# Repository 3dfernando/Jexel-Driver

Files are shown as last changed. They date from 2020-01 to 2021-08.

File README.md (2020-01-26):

# Jexel-Driver
A PIC32-based programmable function generator and solenoid driver with 108 channels. Check 04 - Documentation/SigGen_Board_Datasheet_R02.pdf for usage instructions.

This implementation employs a PIC32MZ2048ECH144 microcontroller to generate 108 independently programmable square waves. The computer interface is an FTDI FT232 chip, which becomes a USB-Serial interface and appears in the computer as a regular COM port. Sending strings to the COM port with the right settings will program/activate the "jexels" (short for jet-pixels), allowing interesting combinations. 

The current effective sampling rate is 49.8kS/s (measured with a scope given the delays of the program), remembering each channel is one-bit. There's a delay of 200ns (one cycle) between the update of each port in the uC. Since there's 10 ports being used, a total 1.8us delay exists between PORTA and PORTK. I deemed this delay insignificant since the maximum square wave drive frequency intended was 200Hz, thus rendering this maximum 1.8us delay less than 0.13 degrees error in the phase between the waves.

Let me know if you find this useful. Things that could be done to improve the application (which I decided not to):
-Increase data density in the serial port to allow a live data stream from the PC instead of a one-off program
-Make drivers with different capacities (more amps, higher voltage, etc) for different solenoid needs
-Isolate better the 24V line from the PIC (i.e., have a connector directly to the driver board).

I used MPLAB X IPE for the microcontroller program. EasyEDA (yes, I'm ashamed) for the electronic boards and JLCPCB for the printing service. The boards were designed to be hand-assembled (I used the hot plate method with solder paste - see here an example https://www.youtube.com/watch?v=2gkZX0r4cvQ).

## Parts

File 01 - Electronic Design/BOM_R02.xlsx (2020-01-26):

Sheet: Motherboard
108-Channel Signal Generator - BOM
Schematic No. | Part Name | Digikey PN | Unit Price | Digikey Link
C1 | CAP CER 0.1UF 16V Y5V 0603 | ‎CL10F104ZO8NNNC‎ | $0.04 | https://www.digikey.com/product-detail/en/samsung-electro-mechanics/CL10F104ZO8NNNC/1276-1258-1-ND/3889344
C2 | CAP CER 0.1UF 16V Y5V 0603 | ‎CL10F104ZO8NNNC‎ | $0.04 | https://www.digikey.com/product-detail/en/samsung-electro-mechanics/CL10F104ZO8NNNC/1276-1258-1-ND/3889344
C3 | CAP CER 0.1UF 16V Y5V 0603 | ‎CL10F104ZO8NNNC‎ | $0.04 | https://www.digikey.com/product-detail/en/samsung-electro-mechanics/CL10F104ZO8NNNC/1276-1258-1-ND/3889344
C4 | CAP CER 0.1UF 16V Y5V 0603 | ‎CL10F104ZO8NNNC‎ | $0.04 | https://www.digikey.com/product-detail/en/samsung-electro-mechanics/CL10F104ZO8NNNC/1276-1258-1-ND/3889344
C5 | CAP CER 0.1UF 16V Y5V 0603 | ‎CL10F104ZO8NNNC‎ | $0.04 | https://www.digikey.com/product-detail/en/samsung-electro-mechanics/CL10F104ZO8NNNC/1276-1258-1-ND/3889344
C6 | CAP CER 0.1UF 16V Y5V 0603 | ‎CL10F104ZO8NNNC‎ | $0.04 | https://www.digikey.com/product-detail/en/samsung-electro-mechanics/CL10F104ZO8NNNC/1276-1258-1-ND/3889344
C7 | CAP CER 0.1UF 16V Y5V 0603 | ‎CL10F104ZO8NNNC‎ | $0.04 | https://www.digikey.com/product-detail/en/samsung-electro-mechanics/CL10F104ZO8NNNC/1276-1258-1-ND/3889344
C8 | CAP CER 0.1UF 16V Y5V 0603 | ‎CL10F104ZO8NNNC‎ | $0.04 | https://www.digikey.com/product-detail/en/samsung-electro-mechanics/CL10F104ZO8NNNC/1276-1258-1-ND/3889344
C9 | CAP CER 0.1UF 16V Y5V 0603 | ‎CL10F104ZO8NNNC‎ | $0.04 | https://www.digikey.com/product-detail/en/samsung-electro-mechanics/CL10F104ZO8NNNC/1276-1258-1-ND/3889344
C10 | CAP CER 0.1UF 16V Y5V 0603 | ‎CL10F104ZO8NNNC‎ | $0.04 | https://www.digikey.com/product-detail/en/samsung-electro-mechanics/CL10F104ZO8NNNC/1276-1258-1-ND/3889344
C11 | CAP CER 10000PF 50V X7R 0603 | ‎CL10B103KB8NNNC | $0.10 | https://www.digikey.com/product-detail/en/samsung-electro-mechanics/CL10B103KB8NNNC/1276-1009-1-ND/3889095
C12 | CAP CER 0.1UF 16V Y5V 0603 | ‎CL10F104ZO8NNNC‎ | $0.04 | https://www.digikey.com/product-detail/en/samsung-electro-mechanics/CL10F104ZO8NNNC/1276-1258-1-ND/3889344
C13 | CAP CER 0.1UF 16V Y5V 0603 | ‎CL10F104ZO8NNNC‎ | $0.04 | https://www.digikey.com/product-detail/en/samsung-electro-mechanics/CL10F104ZO8NNNC/1276-1258-1-ND/3889344
C14 | CAP CER 15PF 50V C0G/NP0 0603 | ‎0603N150J500CT | $0.10 | https://www.digikey.com/product-detail/en/walsin-technology-corporation/0603N150J500CT/1292-1487-1-ND/9355491
C15 | CAP CER 15PF 50V C0G/NP0 0603 | ‎0603N150J500CT | $0.10 | https://www.digikey.com/product-detail/en/walsin-technology-corporation/0603N150J500CT/1292-1487-1-ND/9355491
ICSP | CONN HEADER R/A 6POS 2.54MM | ‎61300611021 | $0.54 | https://www.digikey.com/product-detail/en/w-rth-elektronik/61300611021/732-5339-ND/4846832
J1 | CONN PWR JACK 2X5.5MM SOLDER | ‎PJ-037AH | $0.71 | https://www.digikey.com/product-detail/en/cui-devices/PJ-037AH/CP-037AH-ND/1644547
L1 | FERRITE BEAD 40 OHM 0805 1LN | ‎MI0805K400R-10‎ | $0.21 | https://www.digikey.com/product-detail/en/laird-signal-integrity-products/MI0805K400R-10/240-2389-1-ND/806749
LED1 | LED GREEN DIFFUSED 1206 SMD | ‎QTLP650D4TR | $0.53 | https://www.digikey.com/product-detail/en/everlight-electronics-co-ltd/QTLP650D4TR/1080-1419-1-ND/2676153
PORT1 | CONN RCPT 26POS 0.05 GOLD PCB | ‎20021311-00026T4LF | $2.13 | https://www.digikey.com/product-detail/en/amphenol-icc-fci/20021311-00026T4LF/609-3762-ND/2209113
PORT2 | CONN RCPT 26POS 0.05 GOLD PCB | ‎20021311-00026T4LF | $2.13 | https://www.digikey.com/product-detail/en/amphenol-icc-fci/20021311-00026T4LF/609-3762-ND/2209113
PORT3 | CONN RCPT 26POS 0.05 GOLD PCB | ‎20021311-00026T4LF | $2.13 | https://www.digikey.com/product-detail/en/amphenol-icc-fci/20021311-00026T4LF/609-3762-ND/2209113
PORT4 | CONN RCPT 26POS 0.05 GOLD PCB | ‎20021311-00026T4LF | $2.13 | https://www.digikey.com/product-detail/en/amphenol-icc-fci/20021311-00026T4LF/609-3762-ND/2209113
PORT5 | CONN RCPT 26POS 0.05 GOLD PCB | ‎20021311-00026T4LF | $2.13 | https://www.digikey.com/product-detail/en/amphenol-icc-fci/20021311-00026T4LF/609-3762-ND/2209113
PORT6 | CONN RCPT 26POS 0.05 GOLD PCB | ‎20021311-00026T4LF | $2.13 | https://www.digikey.com/product-detail/en/amphenol-icc-fci/20021311-00026T4LF/609-3762-ND/2209113
R1 | RES SMD 1K OHM 5% 1/4W 0603 | ‎ESR03EZPJ102‎ | $0.10 | https://www.digikey.com/product-detail/en/rohm-semiconductor/ESR03EZPJ102/RHM1.0KDCT-ND/1762924
R2 | RES 10K OHM 1% 1/8W 0603 | ‎RNCP0603FTD10K0 | $0.10 | https://www.digikey.com/product-detail/en/stackpole-electronics-inc/RNCP0603FTD10K0/RNCP0603FTD10K0CT-ND/2240478
R3 | RES SMD 270 OHM 0.5% 1/10W 0805 | ‎RR1220P-271-D | $0.11 | https://www.digikey.com/product-detail/en/susumu/RR1220P-271-D/RR12P270DCT-ND/432816
R4 | RES SMD 270 OHM 0.5% 1/10W 0805 | ‎RR1220P-271-D | $0.11 | https://www.digikey.com/product-detail/en/susumu/RR1220P-271-D/RR12P270DCT-ND/432816
R5 | RES SMD 270 OHM 0.5% 1/10W 0805 | ‎RR1220P-271-D | $0.11 | https://www.digikey.com/product-detail/en/susumu/RR1220P-271-D/RR12P270DCT-ND/432816
RX | LED GREEN DIFFUSED 1206 SMD | ‎QTLP650D4TR | $0.53 | https://www.digikey.com/product-detail/en/everlight-electronics-co-ltd/QTLP650D4TR/1080-1419-1-ND/2676153
TX | LED GREEN DIFFUSED 1206 SMD | ‎QTLP650D4TR | $0.53 | https://www.digikey.com/product-detail/en/everlight-electronics-co-ltd/QTLP650D4TR/1080-1419-1-ND/2676153
U1 | IC MCU 32BIT 2MB FLASH 144LQFP | ‎PIC32MZ2048ECH144-I/PL | $13.07 | https://www.digikey.com/product-detail/en/microchip-technology/PIC32MZ2048ECH144-I-PL/PIC32MZ2048ECH144-I-PL-ND/4500847
U11 | CONN RCPT USB2.0 MICRO B SMD R/A | ‎10118193-0001LF | $0.43 | https://www.digikey.com/product-detail/en/amphenol-icc-fci/10118193-0001LF/609-4616-1-ND/2785380
U8 | IC USB FS SERIAL UART 28-SSOP | ‎FT232RL-REEL‎ | $4.50 | https://www.digikey.com/product-detail/en/ftdi-future-technology-devices-international-ltd/FT232RL-REEL/768-1007-1-ND/1836402
USB_RX | PC TEST POINT NATURAL | ‎S2751-46R | $0.26 | https://www.digikey.com/product-detail/en/harwin-inc/S2751-46R/952-2664-1-ND/5250501
USB_TX | PC TEST POINT NATURAL | ‎S2751-46R | $0.26 | https://www.digikey.com/product-detail/en/harwin-inc/S2751-46R/952-2664-1-ND/5250501
Y1 | CRYSTAL 16.0000MHZ 18PF SMD | ‎ABLS-16.000MHZ-B4-T‎ | $0.36 | https://www.digikey.com/product-detail/en/abracon-llc/ABLS-16.000MHZ-B4-T/535-10226-1-ND/2184261
Total Cost |  |  | $35.98

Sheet: Driver Board
36-Channel Solenoid Driver - BOM
Schematic No. | Part Name | Digikey PN | Unit Price | Digikey Link
P1 | CONN HEADER VERT 26POS 1.27MM | ‎20021111-00026T4LF | $1.52 | https://www.digikey.com/product-detail/en/amphenol-icc-fci/20021111-00026T4LF/609-3720-ND/2209092
P2 | CONN HEADER VERT 26POS 1.27MM | ‎20021111-00026T4LF | $1.52 | https://www.digikey.com/product-detail/en/amphenol-icc-fci/20021111-00026T4LF/609-3720-ND/2209092
U1 | IC PWR DRIVER N-CHAN 1:1 16TSSOP | ‎TPL7407LPWR | $0.68 | https://www.digikey.com/product-detail/en/texas-instruments/TPL7407LPWR/296-37285-1-ND/4733034
U2 | IC PWR DRIVER N-CHAN 1:1 16TSSOP | ‎TPL7407LPWR | $0.68 | https://www.digikey.com/product-detail/en/texas-instruments/TPL7407LPWR/296-37285-1-ND/4733034
U3 | IC PWR DRIVER N-CHAN 1:1 16TSSOP | ‎TPL7407LPWR | $0.68 | https://www.digikey.com/product-detail/en/texas-instruments/TPL7407LPWR/296-37285-1-ND/4733034
U4 | IC PWR DRIVER N-CHAN 1:1 16TSSOP | ‎TPL7407LPWR | $0.68 | https://www.digikey.com/product-detail/en/texas-instruments/TPL7407LPWR/296-37285-1-ND/4733034
U5 | IC PWR DRIVER N-CHAN 1:1 16TSSOP | ‎TPL7407LPWR | $0.68 | https://www.digikey.com/product-detail/en/texas-instruments/TPL7407LPWR/296-37285-1-ND/4733034
U6 | IC PWR DRIVER N-CHAN 1:1 16TSSOP | ‎TPL7407LPWR | $0.68 | https://www.digikey.com/product-detail/en/texas-instruments/TPL7407LPWR/296-37285-1-ND/4733034
F1 | PTC RESET FUSE 30V 300MA 1812 | ‎0ZCG0030FF2C | $0.13 | https://www.digikey.com/product-detail/en/bel-fuse-inc/0ZCG0030FF2C/507-1758-1-ND/4156199
F2 | PTC RESET FUSE 30V 300MA 1812 | ‎0ZCG0030FF2C | $0.13 | https://www.digikey.com/product-detail/en/bel-fuse-inc/0ZCG0030FF2C/507-1758-1-ND/4156199
F3 | PTC RESET FUSE 30V 300MA 1812 | ‎0ZCG0030FF2C | $0.13 | https://www.digikey.com/product-detail/en/bel-fuse-inc/0ZCG0030FF2C/507-1758-1-ND/4156199
F4 | PTC RESET FUSE 30V 300MA 1812 | ‎0ZCG0030FF2C | $0.13 | https://www.digikey.com/product-detail/en/bel-fuse-inc/0ZCG0030FF2C/507-1758-1-ND/4156199
F5 | PTC RESET FUSE 30V 300MA 1812 | ‎0ZCG0030FF2C | $0.13 | https://www.digikey.com/product-detail/en/bel-fuse-inc/0ZCG0030FF2C/507-1758-1-ND/4156199
F6 | PTC RESET FUSE 30V 300MA 1812 | ‎0ZCG0030FF2C | $0.13 | https://www.digikey.com/product-detail/en/bel-fuse-inc/0ZCG0030FF2C/507-1758-1-ND/4156199
J1 | CONN HEADER SMD 12POS 1.5MM | ‎0874371243 | $1.63 | https://www.digikey.com/product-detail/en/molex/0874371243/WM7671CT-ND/717663
J2 | CONN HEADER SMD 12POS 1.5MM | ‎0874371243 | $1.63 | https://www.digikey.com/product-detail/en/molex/0874371243/WM7671CT-ND/717663
J3 | CONN HEADER SMD 12POS 1.5MM | ‎0874371243 | $1.63 | https://www.digikey.com/product-detail/en/molex/0874371243/WM7671CT-ND/717663
J4 | CONN HEADER SMD 12POS 1.5MM | ‎0874371243 | $1.63 | https://www.digikey.com/product-detail/en/molex/0874371243/WM7671CT-ND/717663
J5 | CONN HEADER SMD 12POS 1.5MM | ‎0874371243 | $1.63 | https://www.digikey.com/product-detail/en/molex/0874371243/WM7671CT-ND/717663
J6 | CONN HEADER SMD 12POS 1.5MM | ‎0874371243 | $1.63 | https://www.digikey.com/product-detail/en/molex/0874371243/WM7671CT-ND/717663
Total Cost |  |  | $17.67
Other parts for making cables to connect to solenoids (for 36 channels)
Qty | Part Name | Digikey PN | Unit Price | Digikey Link
6 | CONN HOUSING 12POS 1.5MM W/RAMP | ‎87439-1200 | $0.38 | https://www.digikey.com/product-detail/en/molex/0874391200/23-0874391200-ND/561775
72 | PICO-SPOX 300MM 24AWG PRE-CRIMPE | ‎0797581007 | $0.86 | https://www.digikey.com/product-detail/en/molex/0797581007/WM15690-ND/6564337
36 | CONN HOUSING 2POS 1.5MM W/RAMP | ‎0874390200 | $0.15 | https://www.digikey.com/product-detail/en/molex/0874390200/WM2086-ND/561765
Total Cost |  |  | $69.60

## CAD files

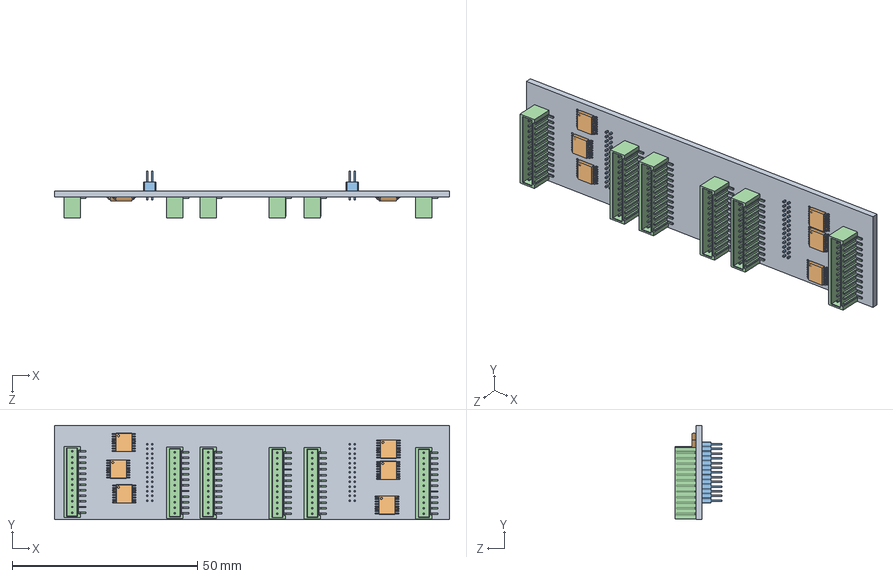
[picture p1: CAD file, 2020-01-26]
02 - 3D Model/01 - Solenoid Driver Board/Driver Board Assembly.SLDASM
106.7 x 25.4 x 12.8 mm
Driver PCB
User Library-TSSOP-16-1 x 6
2002111100026T4LF x 2
Pico-Spox 12w x 6

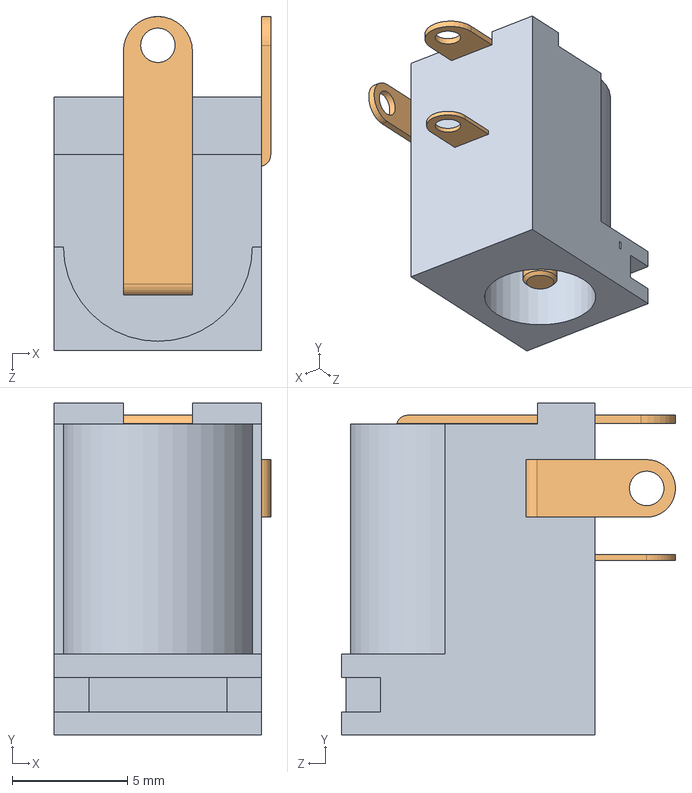
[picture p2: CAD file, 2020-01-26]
02 - 3D Model/02 - Motherboard/Components/User Library-PJ-002AH.sldasm
9.40 x 14.4 x 14.5 mm
User Library-PJ-002AH_Body
User Library-PJ-002AH_Pad

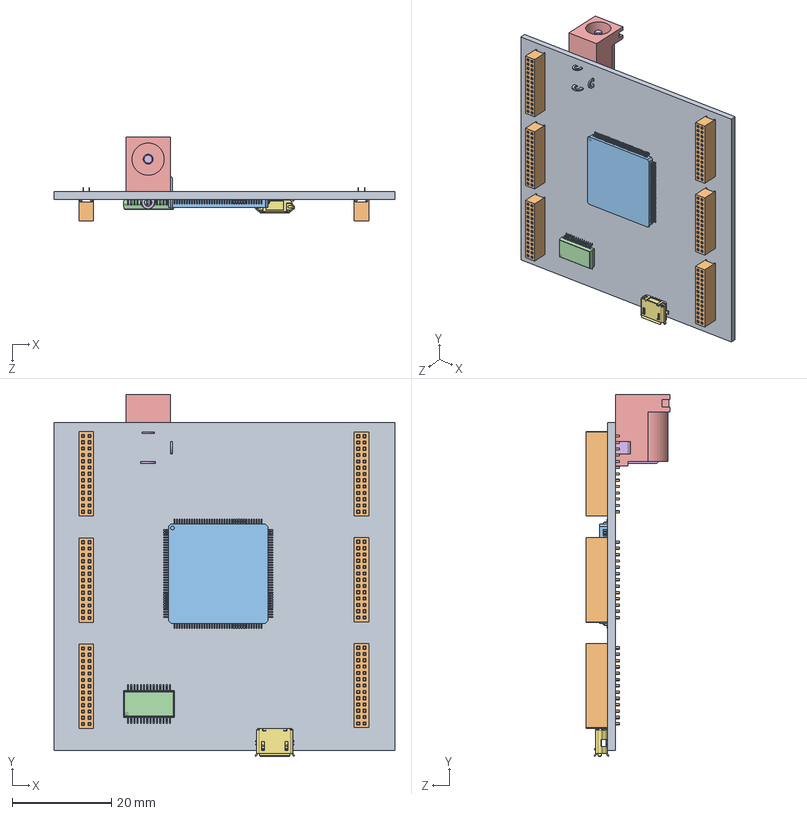
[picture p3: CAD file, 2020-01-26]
02 - 3D Model/02 - Motherboard/Motherboard Assembly.SLDASM
68.6 x 72.9 x 17.0 mm
Motherboard PCB
Header 26 Female x 6
User Library-TQFP144-1
User Library-SSOP-28-1
User Library-PJ-002AH_Body
User Library-PJ-002AH_Pad
usb_mc_2_b_smd

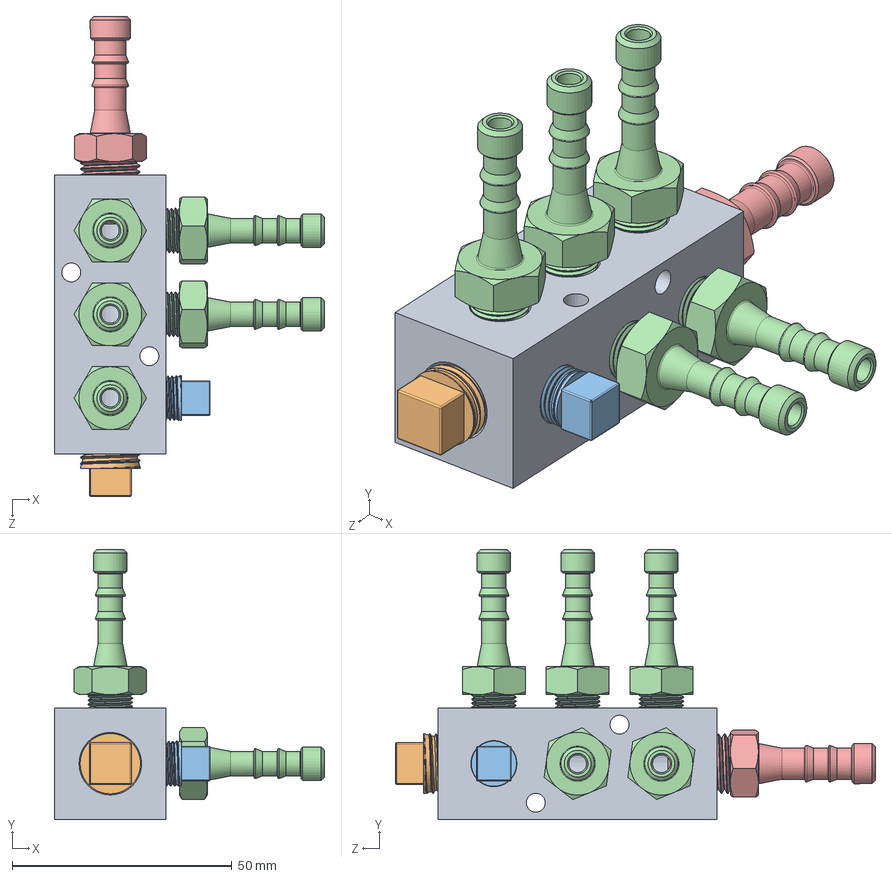
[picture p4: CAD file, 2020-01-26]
02 - 3D Model/03 - Pipelines/Ballast Assembly.SLDASM
61.4 x 61.4 x 109.2 mm
5469K210_BLACK ANODIZED ALUMINUM MANIFOLD
Aluminium Plug 1-4
Aluminium Plug 1-8
Hose Adaptor 1-8 x 1-4 x 5
Hose Adaptor 1-4 x 5-16

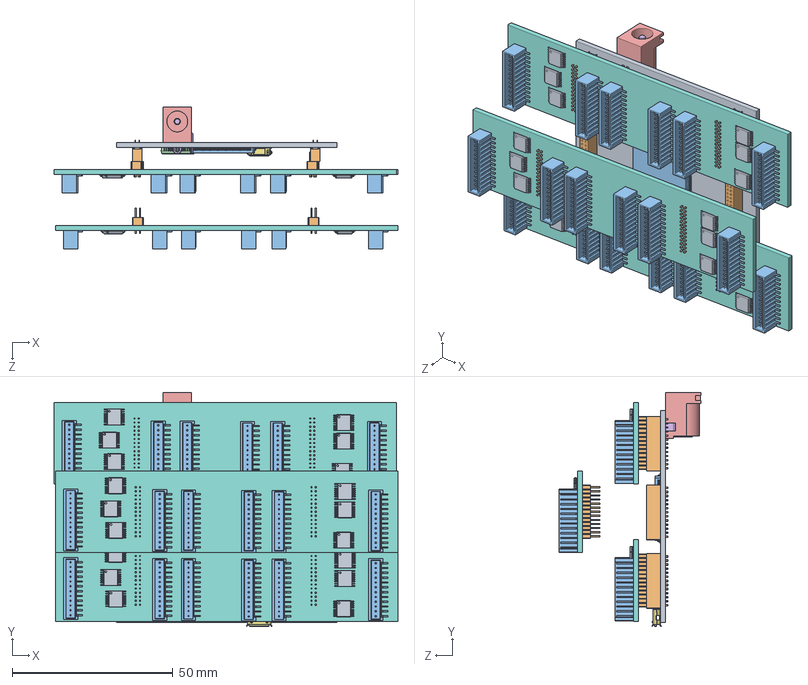
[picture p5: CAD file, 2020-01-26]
02 - 3D Model/Electronic Driver Assembly.SLDASM
107.1 x 72.9 x 44.2 mm
Motherboard PCB
Header 26 Female x 6
User Library-TQFP144-1
User Library-SSOP-28-1
User Library-PJ-002AH_Body
User Library-PJ-002AH_Pad
usb_mc_2_b_smd
Driver PCB x 3
User Library-TSSOP-16-1 x 18
2002111100026T4LF x 6
Pico-Spox 12w x 18

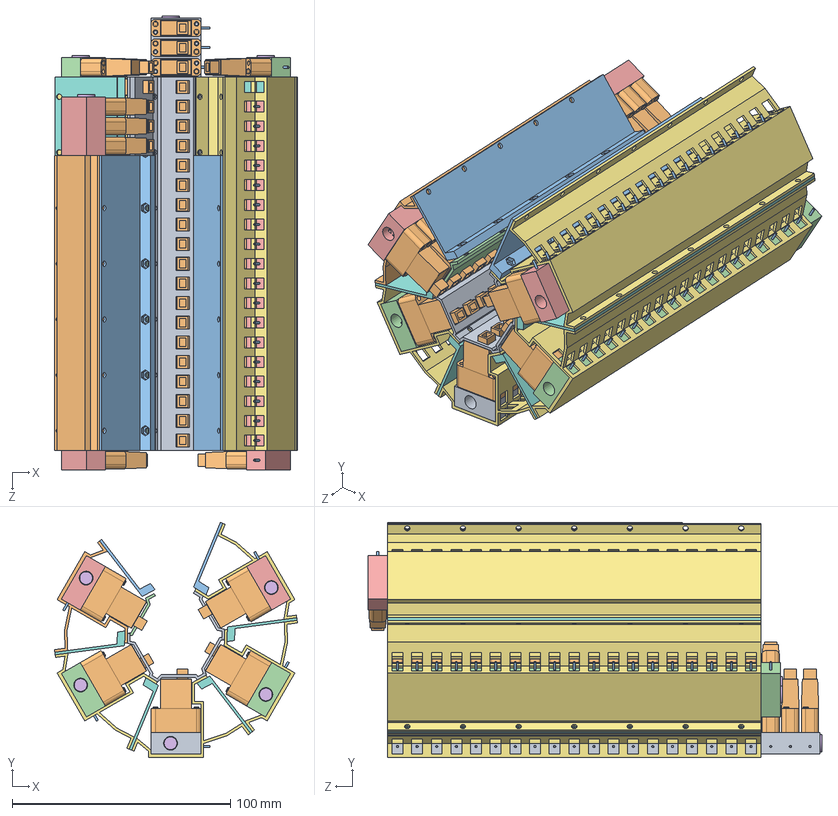
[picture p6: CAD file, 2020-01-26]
02 - 3D Model/Manifold Assembly Assembly.SLDASM
111.4 x 107.8 x 208.0 mm
Manifold 01 R00
Microvalv x 100
Tubing_1 x 100
Manifold 02 R00 x 2
Manifold 03 R00 x 2
EndPlug x 5
Valve Support Channel 2 x 4
Valve Support Channel 1 x 3
Valve Support Channel 3 x 3
Valve Support Channel Shorter 1 x 2
Valve Support Channel Shorter 2 x 2
Valve Support Channel Shorter 3 x 2

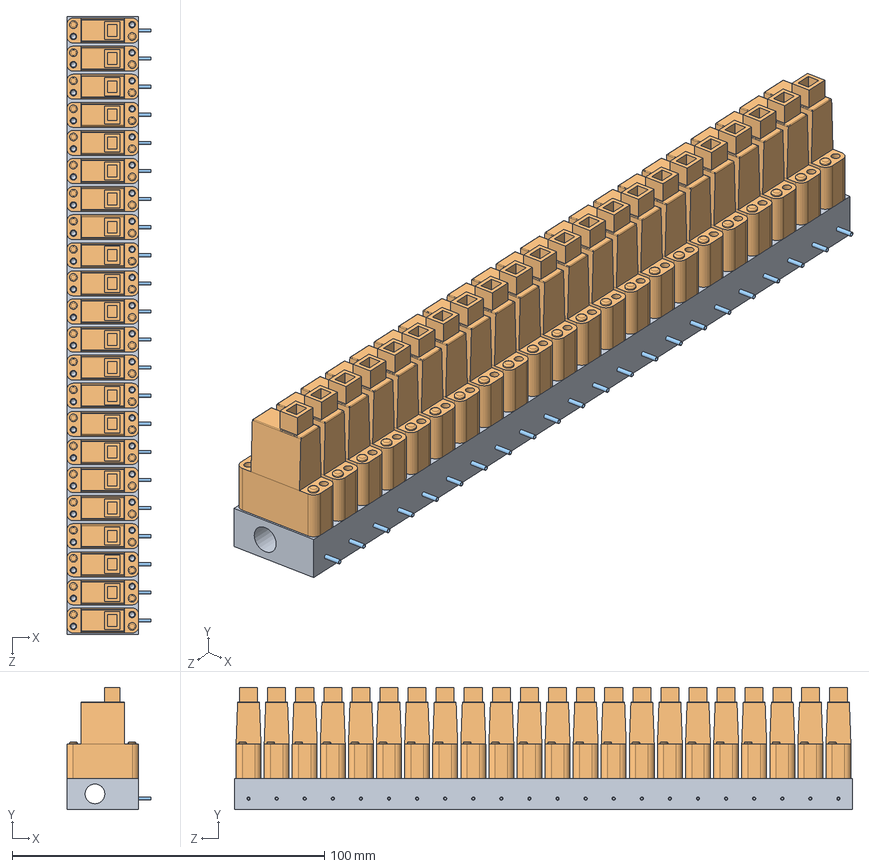
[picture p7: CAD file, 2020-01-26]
02 - 3D Model/Manifold Assembly 01.SLDASM
27.0 x 39.1 x 198.0 mm
Manifold 01 R00
Microvalv x 22
Tubing_1 x 22

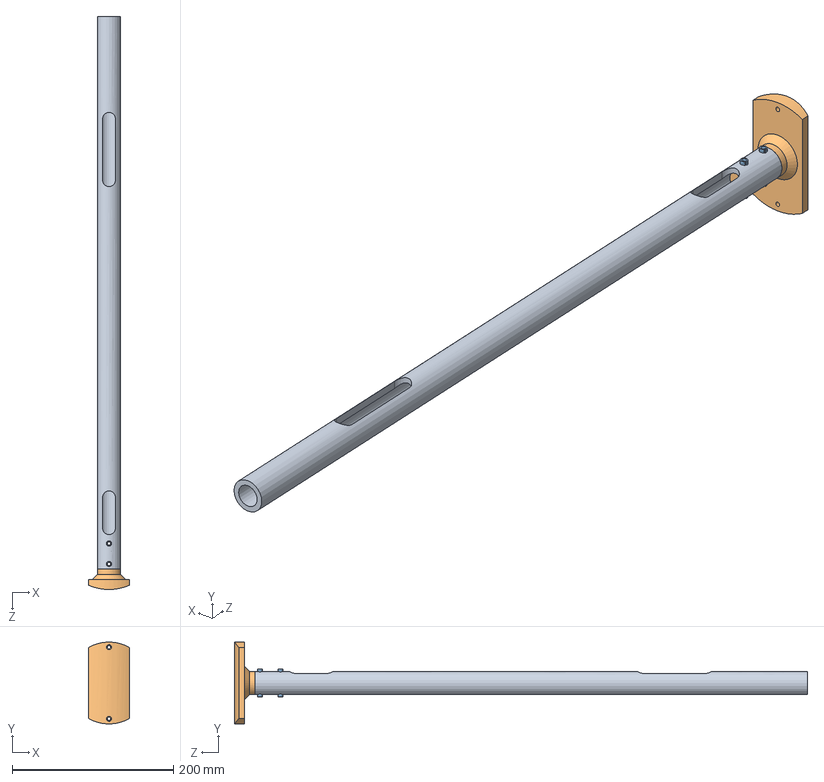
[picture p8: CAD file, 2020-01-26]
02 - 3D Model/lofted_cyl_strut.SLDASM
50.8 x 101.6 x 711.2 mm
Lofted_cyl_support_strut
Lofted_cyl_support_flange_v2
92383A750_TYPE 420 STAINLESS STEEL SLOTTED SPRING PIN x 2

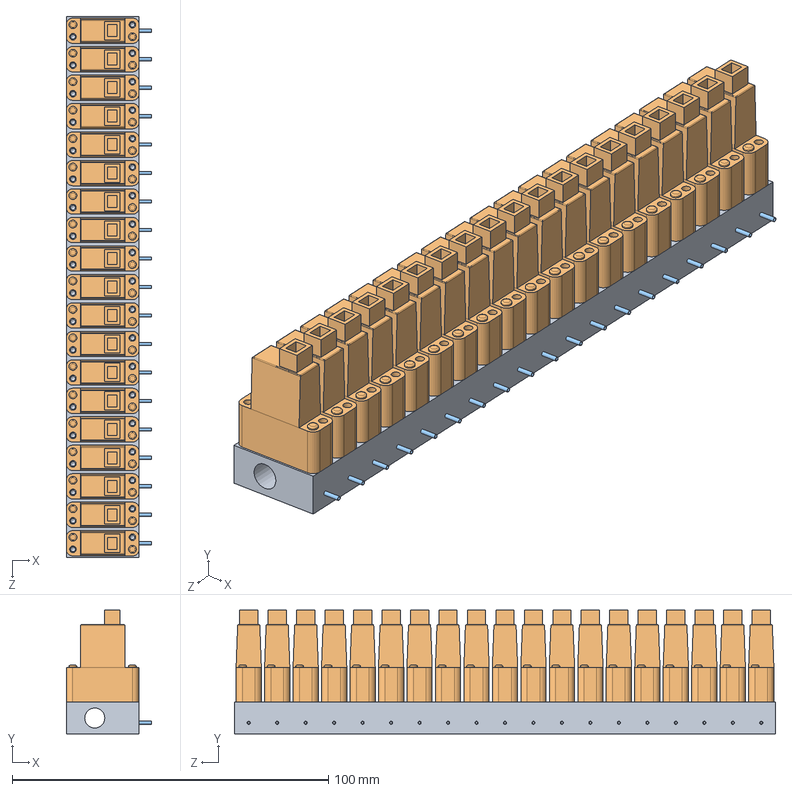
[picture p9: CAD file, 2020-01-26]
02 - 3D Model/Manifold Assembly 03.SLDASM
27.0 x 39.1 x 171.0 mm
Manifold 03 R00
Microvalv x 19
Tubing_1 x 19

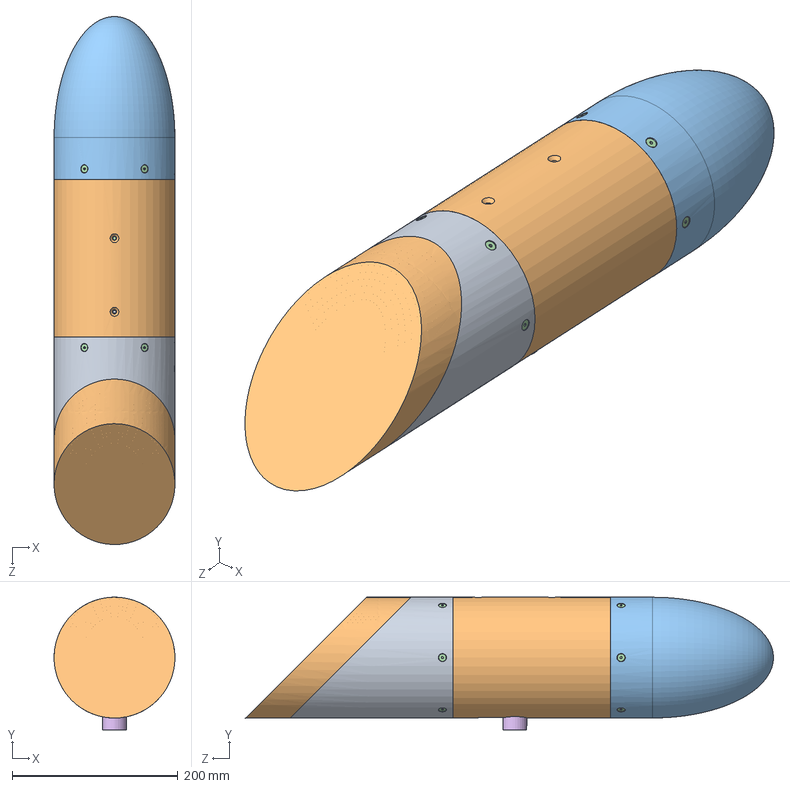
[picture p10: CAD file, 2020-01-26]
02 - 3D Model/lofted_cyl_45_assembly.SLDASM
146.1 x 160.3 x 638.1 mm
Lofted_cyl_afterbody_45deg - v2
Lofted_cyl_middle
Lofted_cyl_nosecone
91253A192_ALLOY STEEL FLAT-HEAD SOCKET CAP SCREW x 12
91253A104_ALLOY STEEL FLAT-HEAD SOCKET CAP SCREW x 8
Lofted_cyl_support_strut
Lofted_cyl_support_flange_v2
92383A750_TYPE 420 STAINLESS STEEL SLOTTED SPRING PIN x 2
Manifold 01 R00
Microvalv x 98
Tubing_1 x 100
Manifold 02 R00 x 2
Manifold 03 R00 x 2
EndPlug x 5
Valve Support Channel 2 x 4
Valve Support Channel 1 x 3
Valve Support Channel 3 x 3
Valve Support Channel Shorter 1 x 2
Valve Support Channel Shorter 2 x 2
Valve Support Channel Shorter 3 x 2
Motherboard PCB
Header 26 Female x 6
User Library-TQFP144-1
User Library-SSOP-28-1
User Library-PJ-002AH_Body
User Library-PJ-002AH_Pad
usb_mc_2_b_smd
Driver PCB x 3
User Library-TSSOP-16-1 x 18
2002111100026T4LF x 6
Pico-Spox 12w x 18
Spacer 1 x 2
Spacer 2
Actuator Plate 45deg 324jx
Revolver

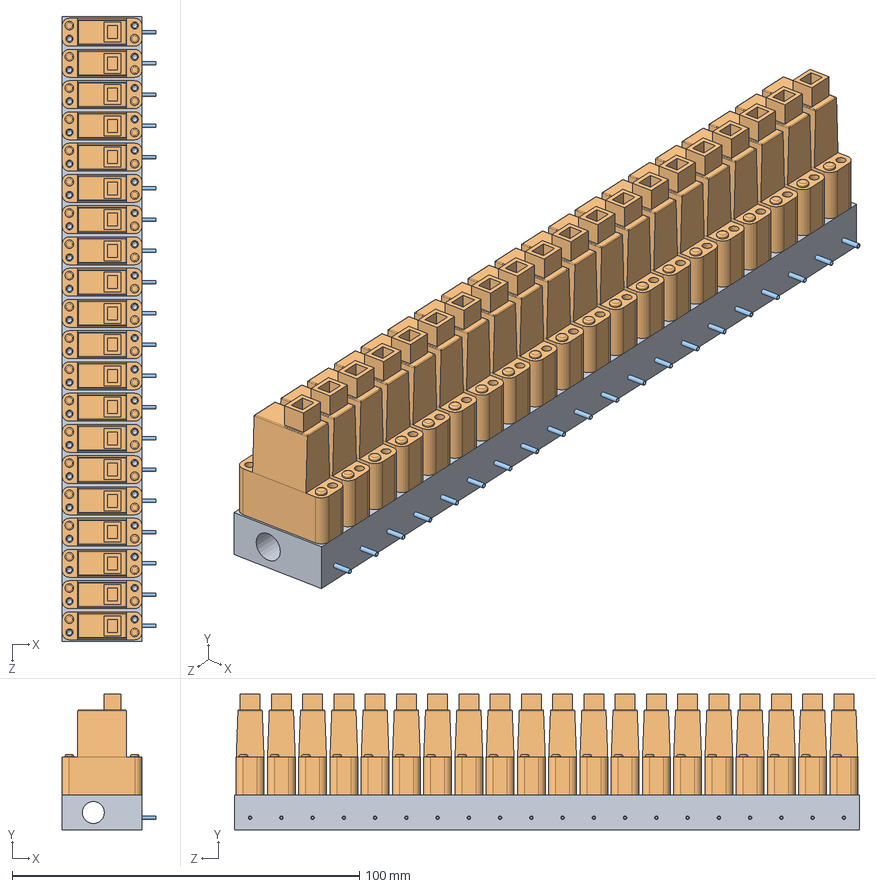
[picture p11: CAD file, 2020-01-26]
02 - 3D Model/Manifold Assembly 02.SLDASM
27.0 x 39.1 x 180.0 mm
Manifold 02 R00
Microvalv x 20
Tubing_1 x 20

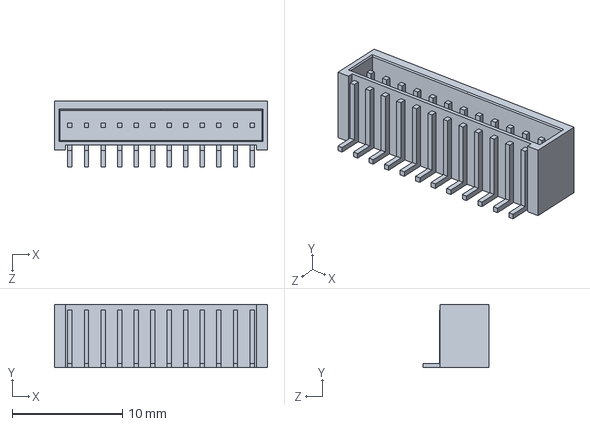
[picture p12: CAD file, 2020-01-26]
02 - 3D Model/01 - Solenoid Driver Board/Components/Pico-Spox 12w.SLDPRT
19.3 x 5.75 x 6.00 mm

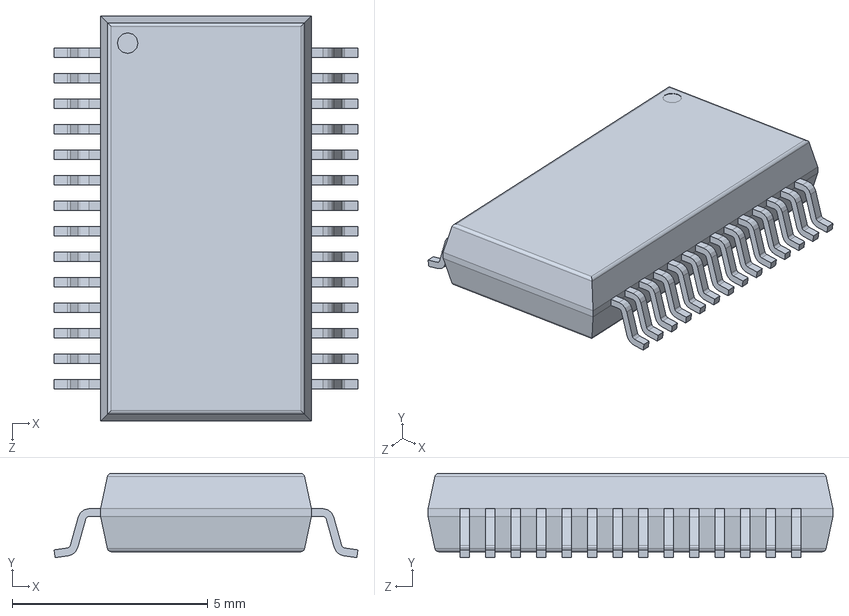
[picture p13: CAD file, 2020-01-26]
02 - 3D Model/02 - Motherboard/Components/User Library-SSOP-28-1.SLDPRT
7.76 x 2.15 x 10.3 mm

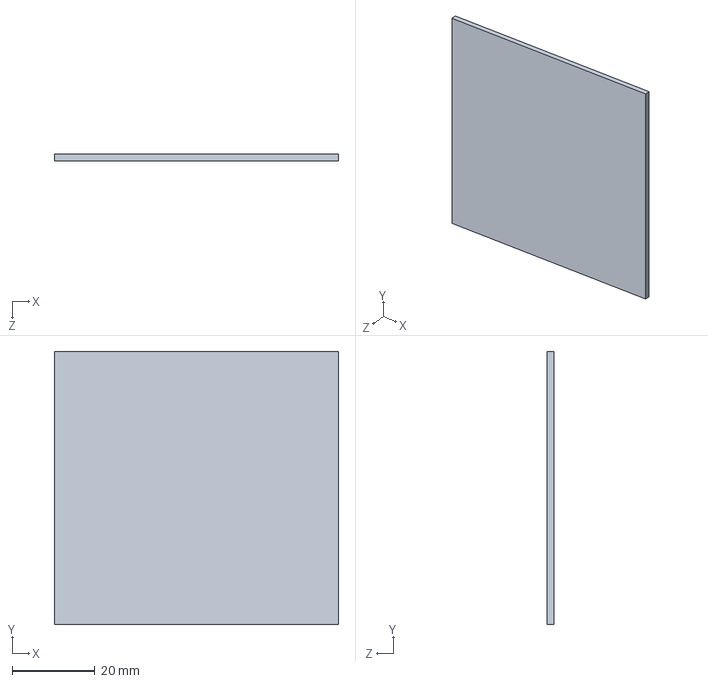
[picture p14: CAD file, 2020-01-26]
02 - 3D Model/02 - Motherboard/Motherboard PCB.SLDPRT
68.6 x 66.0 x 1.60 mm

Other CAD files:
02 - 3D Model/03 - Pipelines/Brass Tee 1-4 x 1-4.SLDPRT
02 - 3D Model/Lofted_cyl_nosecone.SLDPRT
02 - 3D Model/01 - Solenoid Driver Board/Components/User Library-TSSOP-16-1.SLDPRT
02 - 3D Model/01 - Solenoid Driver Board/Driver PCB.SLDPRT
02 - 3D Model/01 - Solenoid Driver Board/Components/2002111100026T4LF.SLDPRT
02 - 3D Model/01 - Solenoid Driver Board/Components/6045.SLDPRT
02 - 3D Model/02 - Motherboard/Components/Header 26 Female.SLDPRT
02 - 3D Model/02 - Motherboard/Components/User Library-TQFP144-1.SLDPRT
02 - 3D Model/02 - Motherboard/Components/usb_mc_2_b_smd.SLDPRT
02 - 3D Model/03 - Pipelines/5469K210_BLACK ANODIZED ALUMINUM MANIFOLD.SLDPRT
02 - 3D Model/03 - Pipelines/Aluminium Plug 1-4.SLDPRT
02 - 3D Model/03 - Pipelines/Aluminium Plug 1-8.SLDPRT
02 - 3D Model/03 - Pipelines/Brass 90 Elbow 1-4.SLDPRT
02 - 3D Model/03 - Pipelines/Brass 90 Elbow 1-8.SLDPRT
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

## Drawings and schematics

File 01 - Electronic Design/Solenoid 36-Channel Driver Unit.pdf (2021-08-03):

8/3/2021 | Solenoid 36-Channel Driver Unit

+24V

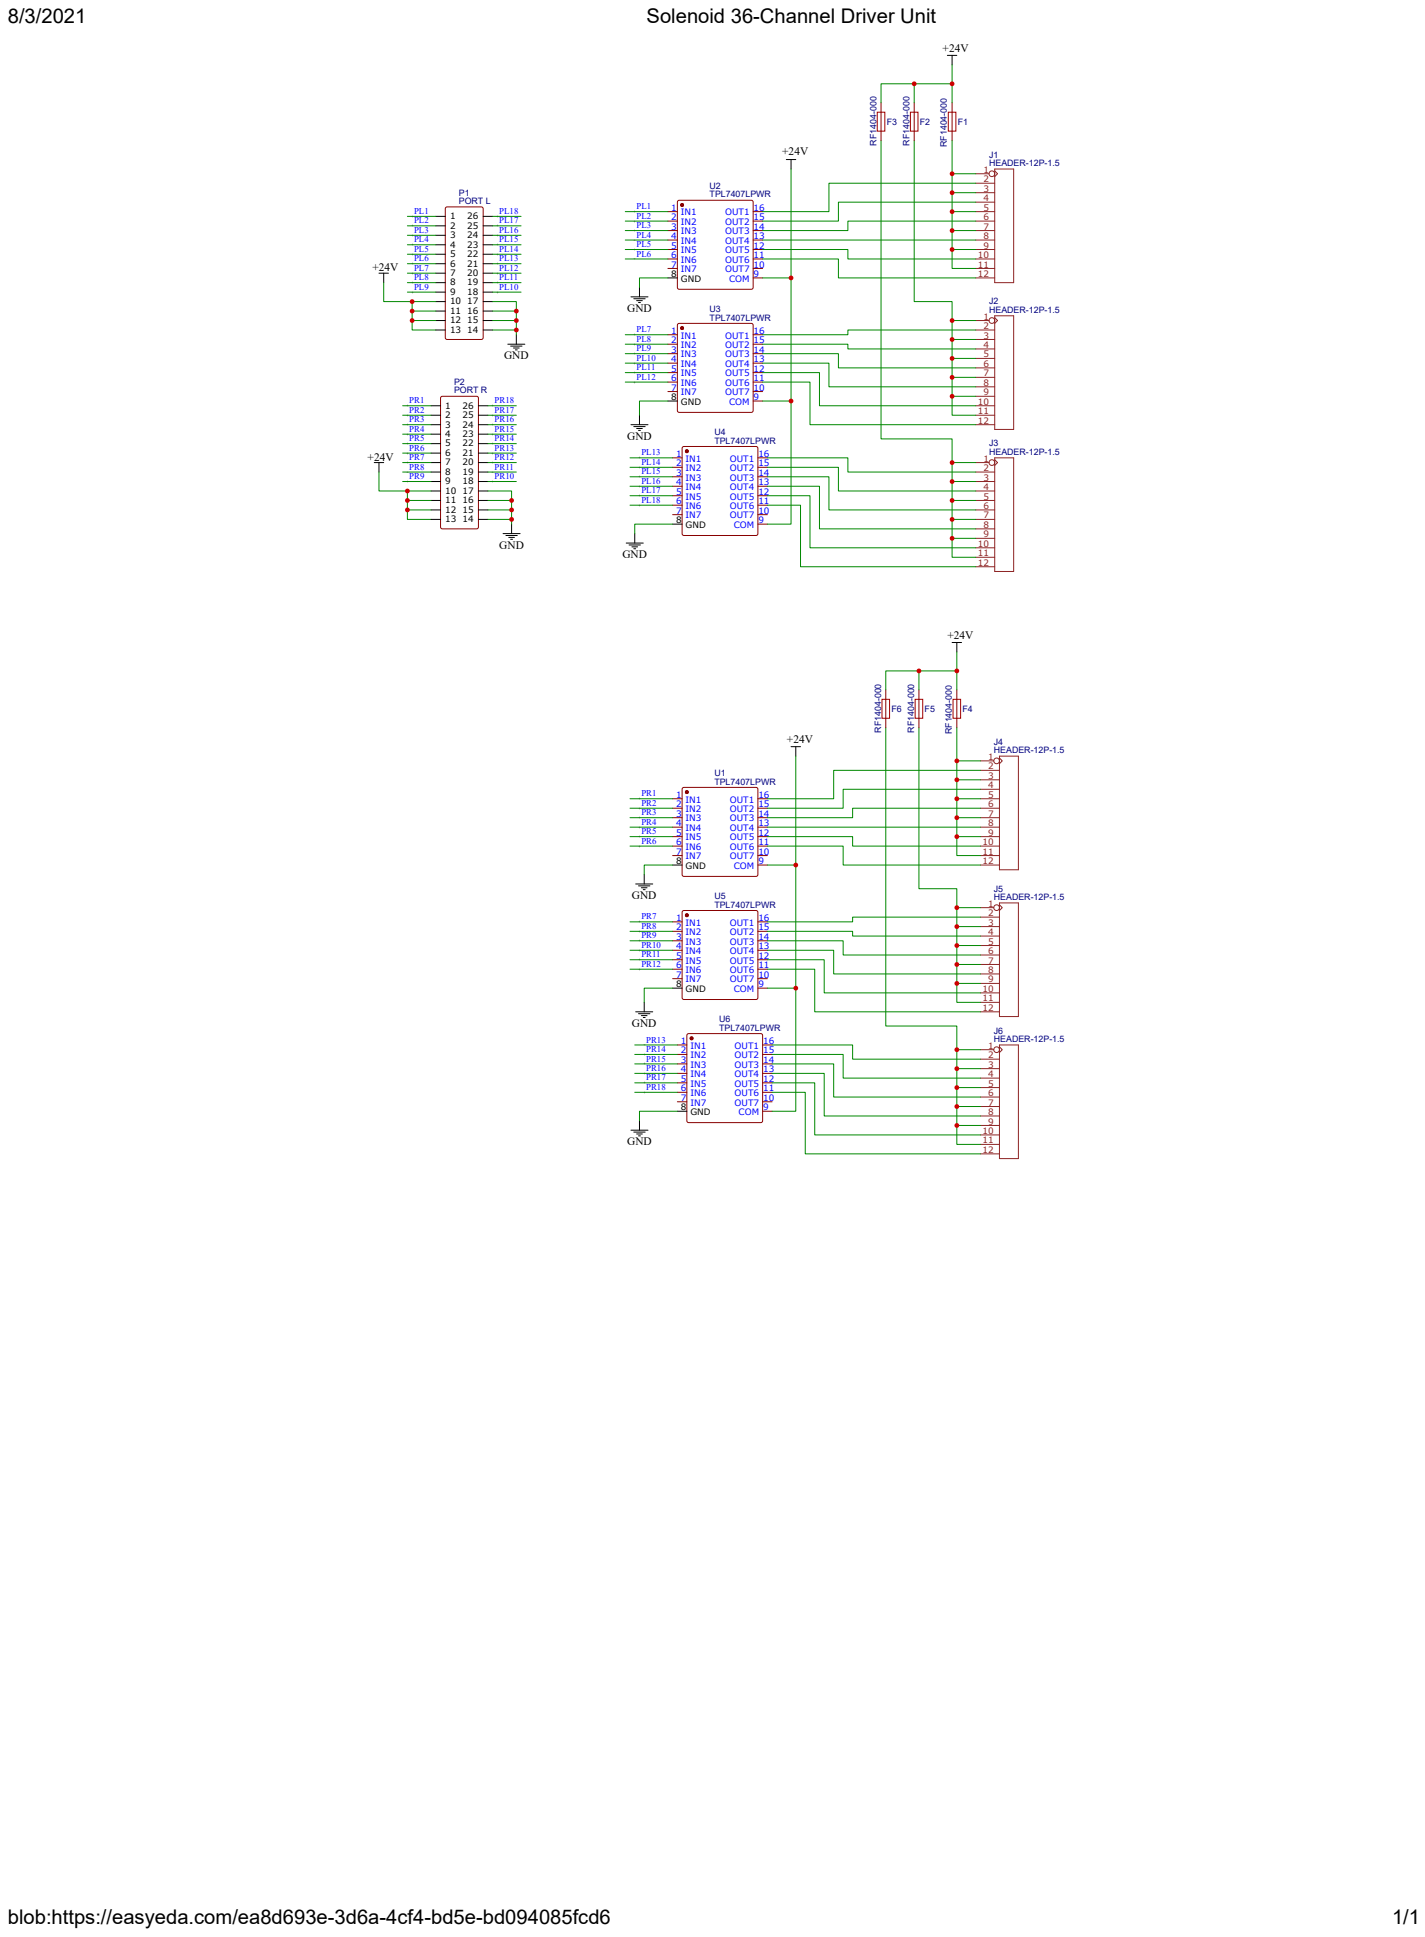
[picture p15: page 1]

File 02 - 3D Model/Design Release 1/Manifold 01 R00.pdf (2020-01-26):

F

B

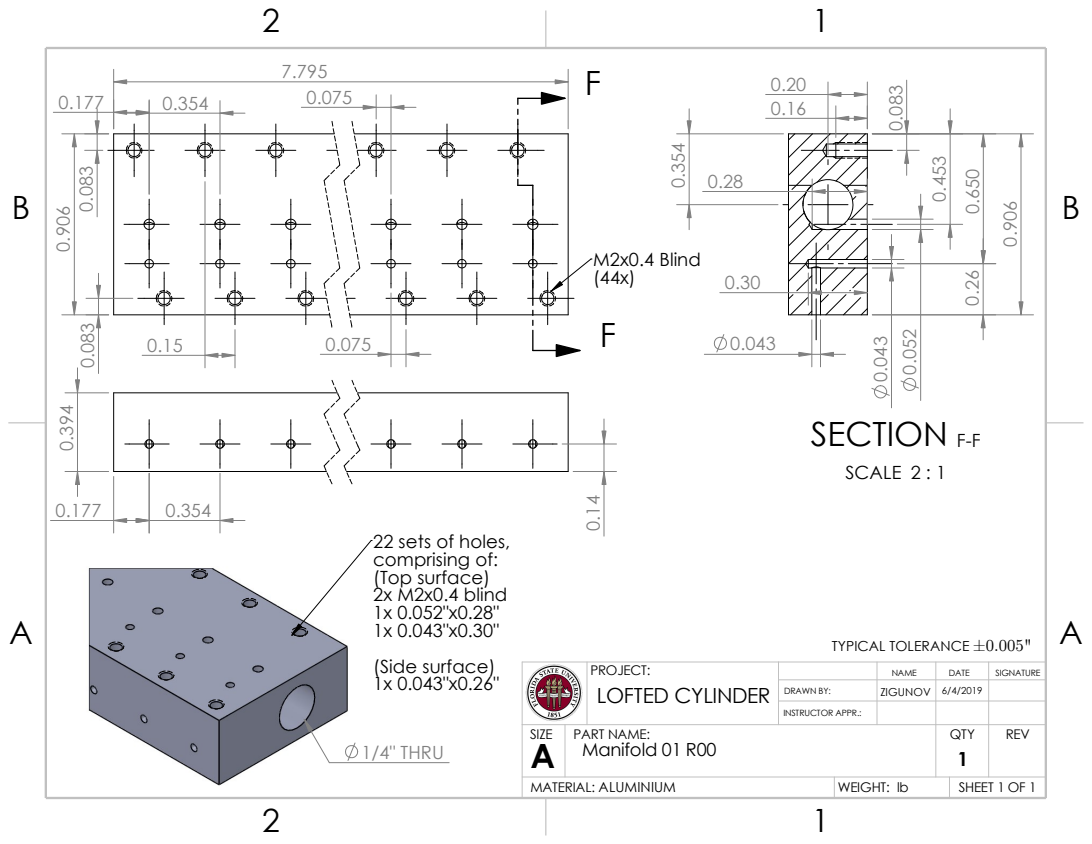
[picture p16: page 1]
TYPICAL TOLERANCE ±0.005"; M2x0.4 Blind (44x); 1/4" THRU; 22 sets of holes, comprising of: (Top surface) 2x M2x0.4 blind 1x 0.052"x0.28" 1x 0.043"x0.30"; (Side surface) 1x 0.043"x0.26"; SECTION F-F; SCALE 2 : 1

PROJECT: LOFTED CYLINDER | | NAME | DATE | SIGNATURE

DRAWN BY: | ZIGUNOV | 6/4/2019

INSTRUCTOR APPR.:

SIZE A | PART NAME: Manifold 01 R00 | QTY 1 | REV

ALUMINIUM MATERIAL: | WEIGHT: lb | SHEET 1 OF 1

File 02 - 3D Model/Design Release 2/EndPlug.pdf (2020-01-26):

B

B

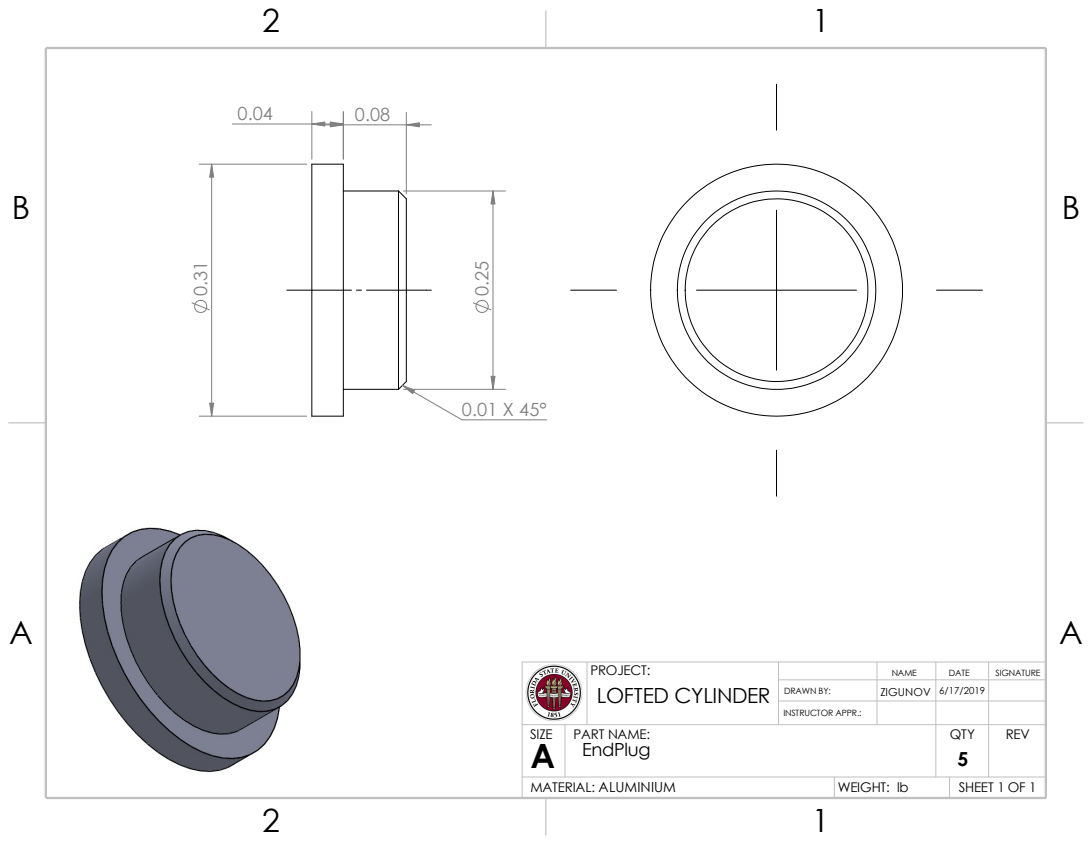
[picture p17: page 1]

PROJECT: | | NAME | DATE | SIGNATURE
DRAWN BY: | ZIGUNOV LOFTED CYLINDER | 6/17/2019
SIZE A | PART NAME: EndPlug | QTY 5 | REV

INSTRUCTOR APPR.:

ALUMINIUM MATERIAL: | WEIGHT: lb | SHEET 1 OF 1

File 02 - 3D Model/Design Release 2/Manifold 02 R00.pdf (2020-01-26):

B

B

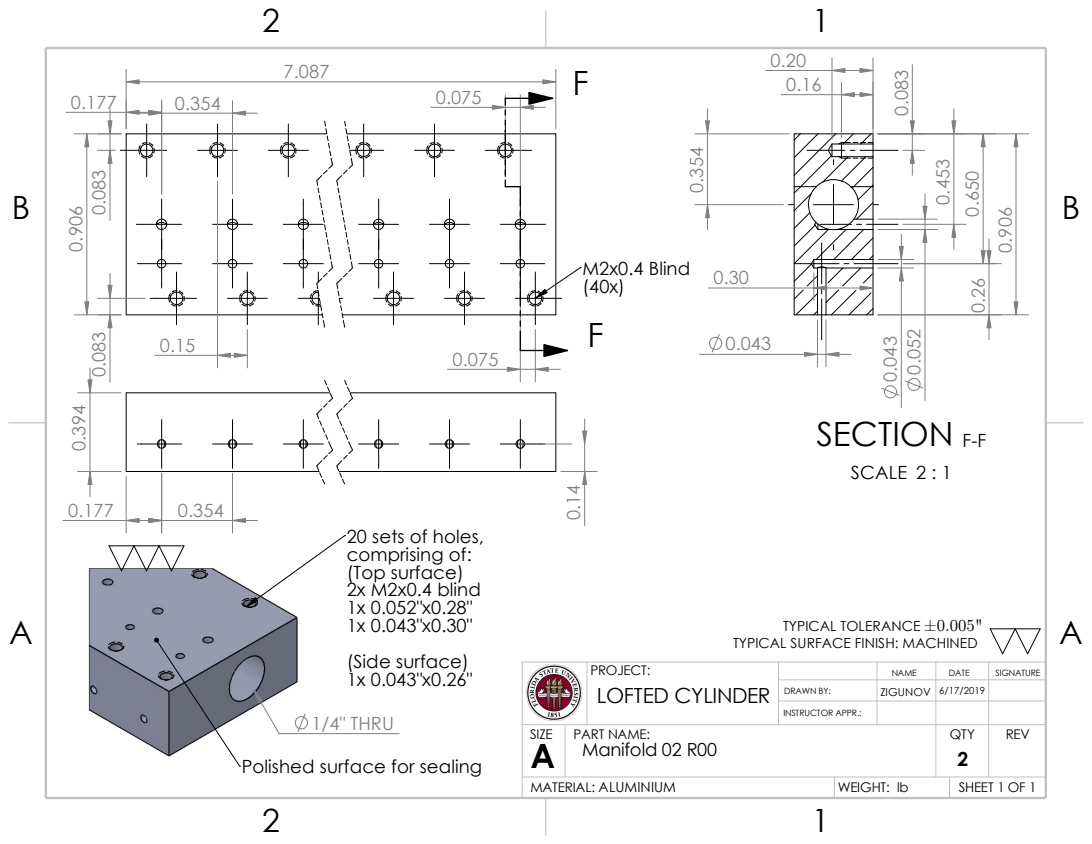
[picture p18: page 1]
M2x0.4 Blind (40x) 0.083; TYPICAL TOLERANCE ±0.005" ⁰.14 0.177 ⁰.394; (Side surface) 1x 0.043"x0.26"; 20 sets of holes, comprising of: (Top surface) 2x M2x0.4 blind 1x 0.052"x0.28" 1x 0.043"x0.30"; 1/4" THRU; SECTION F-F; SCALE 2 : 1

TYPICAL SURFACE FINISH: MACHINED

PROJECT: LOFTED CYLINDER | | NAME | DATE | SIGNATURE

DRAWN BY: | ZIGUNOV | 6/17/2019

INSTRUCTOR APPR.:

SIZE A | PART NAME: Manifold 02 R00 | QTY 2 | REV

Polished surface for sealing

ALUMINIUM MATERIAL: | WEIGHT: lb | SHEET 1 OF 1

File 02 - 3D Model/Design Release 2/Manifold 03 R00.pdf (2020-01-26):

B

B

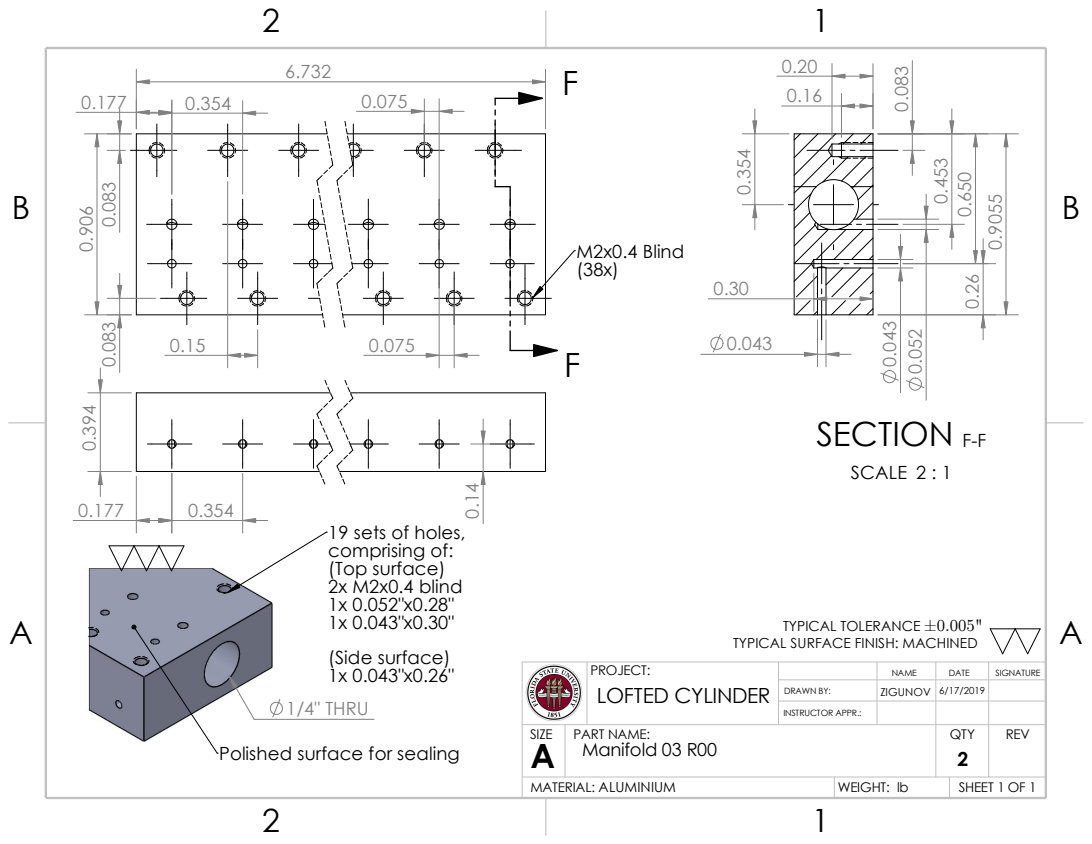
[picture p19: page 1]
TYPICAL TOLERANCE ±0.005"; SECTION F-F; SCALE 2 : 1 ⁰.052; M2x0.4 Blind (38x) 0.083; (Side surface) 1x 0.043"x0.26"; 19 sets of holes, comprising of: (Top surface) 2x M2x0.4 blind 1x 0.052"x0.28" 1x 0.043"x0.30"; 1/4" THRU

TYPICAL SURFACE FINISH: MACHINED

PROJECT: LOFTED CYLINDER | | NAME | DATE | SIGNATURE

DRAWN BY: | ZIGUNOV | 6/17/2019

INSTRUCTOR APPR.:

SIZE A | PART NAME: Manifold 03 R00 | QTY 2 | REV

Polished surface for sealing

ALUMINIUM MATERIAL: | WEIGHT: lb | SHEET 1 OF 1

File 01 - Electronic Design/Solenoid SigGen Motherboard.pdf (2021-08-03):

8/3/2021 | Solenoid SigGen Motherboard

### VCC

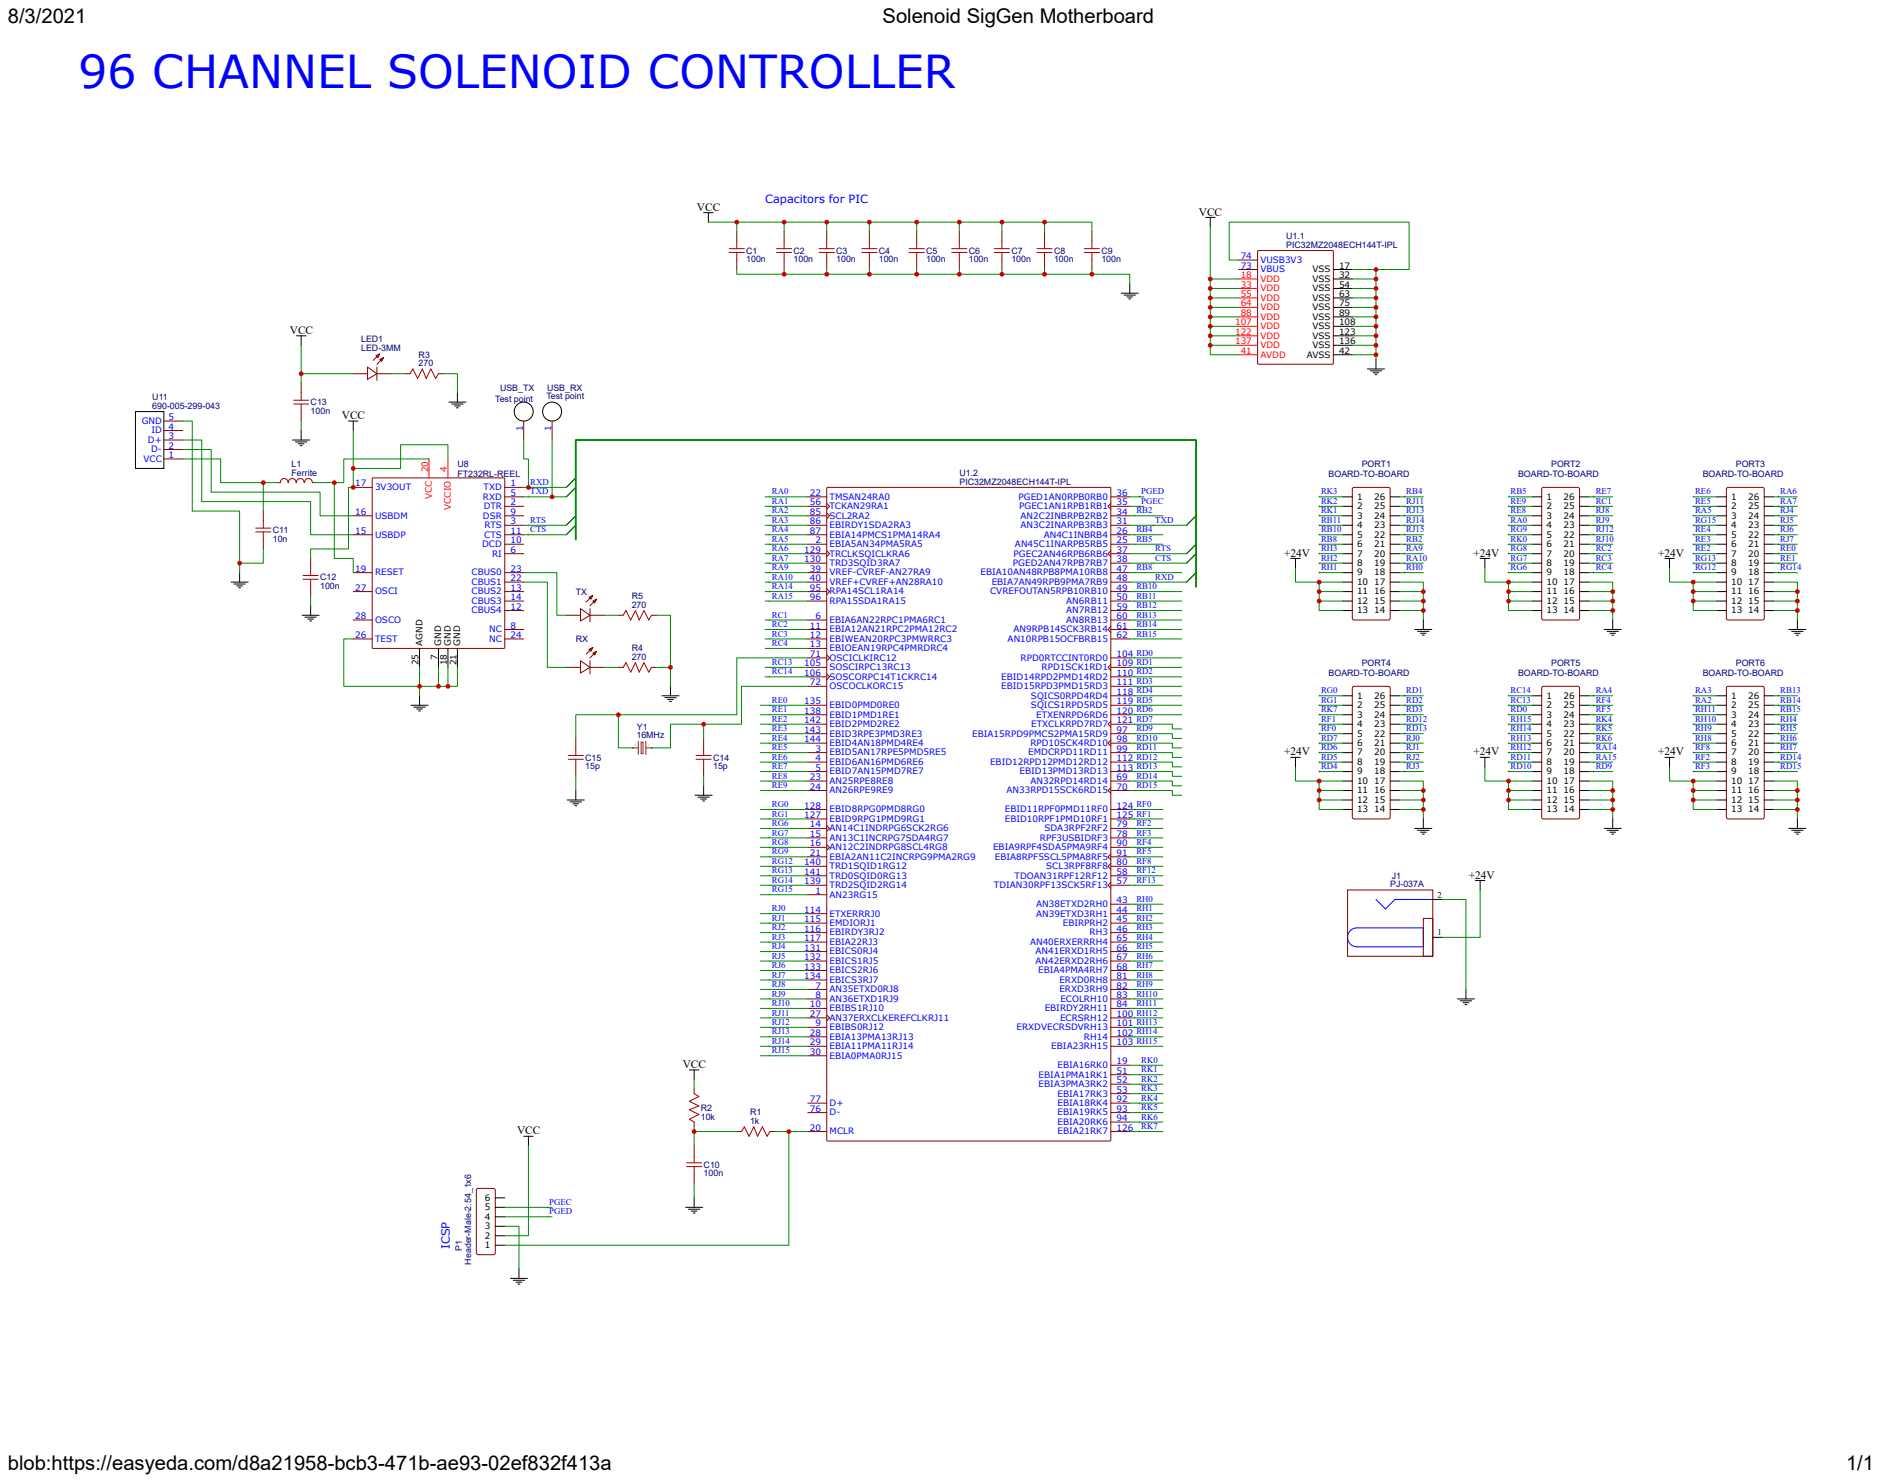
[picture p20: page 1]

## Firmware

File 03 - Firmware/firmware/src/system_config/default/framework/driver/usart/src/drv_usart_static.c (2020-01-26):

/*******************************************************************************
  USART Driver Static implementation

  Company:
    Microchip Technology Inc.

  File Name:
    drv_usart_static.c

  Summary:
    Source code for the USART driver static implementation.

  Description:
    The USART device driver provides a simple interface to manage the USART
    modules on Microchip microcontrollers. This file contains static implementation
    for the USART driver.

  Remarks:
    Static interfaces incorporate the driver instance number within the names
    of the routines, eliminating the need for an object ID or object handle.

    Static single-open interfaces also eliminate the need for the open handle.
*******************************************************************************/

//DOM-IGNORE-BEGIN
/*******************************************************************************
Copyright (c) 2015 released Microchip Technology Inc.  All rights reserved.

Microchip licenses to you the right to use, modify, copy and distribute
Software only when embedded on a Microchip microcontroller or digital signal
controller that is integrated into your product or third party product
(pursuant to the sublicense terms in the accompanying license agreement).

You should refer to the license agreement accompanying this Software for
additional information regarding your rights and obligations.

SOFTWARE AND DOCUMENTATION ARE PROVIDED AS IS WITHOUT WARRANTY OF ANY KIND,
EITHER EXPRESS OR IMPLIED, INCLUDING WITHOUT LIMITATION, ANY WARRANTY OF
MERCHANTABILITY, TITLE, NON-INFRINGEMENT AND FITNESS FOR A PARTICULAR PURPOSE.
IN NO EVENT SHALL MICROCHIP OR ITS LICENSORS BE LIABLE OR OBLIGATED UNDER
CONTRACT, NEGLIGENCE, STRICT LIABILITY, CONTRIBUTION, BREACH OF WARRANTY, OR
OTHER LEGAL EQUITABLE THEORY ANY DIRECT OR INDIRECT DAMAGES OR EXPENSES
INCLUDING BUT NOT LIMITED TO ANY INCIDENTAL, SPECIAL, INDIRECT, PUNITIVE OR
CONSEQUENTIAL DAMAGES, LOST PROFITS OR LOST DATA, COST OF PROCUREMENT OF
SUBSTITUTE GOODS, TECHNOLOGY, SERVICES, OR ANY CLAIMS BY THIRD PARTIES
(INCLUDING BUT NOT LIMITED TO ANY DEFENSE THEREOF), OR OTHER SIMILAR COSTS.
*******************************************************************************/
//DOM-IGNORE-END

// *****************************************************************************
// *****************************************************************************
// Section: Included Files
// *****************************************************************************
// *****************************************************************************

#include "system_config.h"
#include "system_definitions.h"


// *****************************************************************************
// *****************************************************************************
// Section: Global Data
// *****************************************************************************
// *****************************************************************************

/* This is the driver static object . */
DRV_USART_OBJ  gDrvUSART0Obj ;

// *****************************************************************************
// *****************************************************************************
// Section: Instance 0 static driver functions
// *****************************************************************************
// *****************************************************************************

SYS_MODULE_OBJ DRV_USART0_Initialize(void)
{
    uint32_t clockSource;

    /* Disable the USART module to configure it*/
    PLIB_USART_Disable (USART_ID_1);

    /* Initialize the USART based on configuration settings */
    PLIB_USART_InitializeModeGeneral(USART_ID_1,
            false,  /*Auto baud*/
            false,  /*LoopBack mode*/
            false,  /*Auto wakeup on start*/
            false,  /*IRDA mode*/
            false);  /*Stop In Idle mode*/

    /* Set the line control mode */
    PLIB_USART_LineControlModeSelect(USART_ID_1, DRV_USART_LINE_CONTROL_8NONE1);

    /* We set the receive interrupt mode to receive an interrupt whenever FIFO
       is not empty */
    PLIB_USART_InitializeOperation(USART_ID_1,
            USART_RECEIVE_FIFO_ONE_CHAR,
            USART_TRANSMIT_FIFO_IDLE,
            USART_ENABLE_TX_RX_USED);

    /* Get the USART clock source value*/
    clockSource = SYS_CLK_PeripheralFrequencyGet ( CLK_BUS_PERIPHERAL_2 );

    /* Set the baud rate and enable the USART */
    PLIB_USART_BaudSetAndEnable(USART_ID_1,
            clockSource,
            57600);  /*Desired Baud rate value*/

    /* Return the driver instance value*/
    return (SYS_MODULE_OBJ)DRV_USART_INDEX_0;
}

void  DRV_USART0_Deinitialize(void)
{
    /* Disable USART module */
    PLIB_USART_Disable (USART_ID_1);

}


SYS_STATUS DRV_USART0_Status(void)
{
    /* Return the status as ready always */
    return SYS_STATUS_READY;
}

DRV_HANDLE DRV_USART0_Open(const SYS_MODULE_INDEX index, const DRV_IO_INTENT ioIntent)
{

    /* Return the driver instance value*/
    return ((DRV_HANDLE)DRV_USART_INDEX_0 );
}

void DRV_USART0_Close(void)
{
    return;
}

DRV_USART_CLIENT_STATUS DRV_USART0_ClientStatus(void)
{
    /* Return the status as ready always*/
    return DRV_USART_CLIENT_STATUS_READY;
}

DRV_USART_TRANSFER_STATUS DRV_USART0_TransferStatus( void )
{
    DRV_USART_TRANSFER_STATUS result = 0;

    /* Check if RX data available */
    if(PLIB_USART_ReceiverDataIsAvailable(USART_ID_1))
    {
        result|= DRV_USART_TRANSFER_STATUS_RECEIVER_DATA_PRESENT;
    }
    else
    {
        result|= DRV_USART_TRANSFER_STATUS_RECEIVER_EMPTY;
    }

    /* Check if TX Buffer is empty */
    if(PLIB_USART_TransmitterIsEmpty(USART_ID_1))
    {
        result|= DRV_USART_TRANSFER_STATUS_TRANSMIT_EMPTY;
    }

    /* Check if the TX buffer is full */
    if(PLIB_USART_TransmitterBufferIsFull(USART_ID_1))
    {
        result|= DRV_USART_TRANSFER_STATUS_TRANSMIT_FULL;
    }

    return(result);
}

DRV_USART_ERROR DRV_USART0_ErrorGet(void)
{
    DRV_USART_ERROR error;
    error = gDrvUSART0Obj.error;

    /* Clear the error before returning */
    gDrvUSART0Obj.error = DRV_USART_ERROR_NONE;

    /* Return the error*/
    return(error);
}


void _DRV_USART0_ErrorConditionClear()
{
    uint8_t dummyData = 0u;
    /* RX length = (FIFO level + RX register) */
    uint8_t RXlength = _DRV_USART_RX_DEPTH;

    /* If it's a overrun error then clear it to flush FIFO */
    if(USART_ERROR_RECEIVER_OVERRUN & PLIB_USART_ErrorsGet(USART_ID_1))
    {
        PLIB_USART_ReceiverOverrunErrorClear(USART_ID_1);
    }

    /* Read existing error bytes from FIFO to clear parity and framing error flags*/
    while( (USART_ERROR_PARITY | USART_ERROR_FRAMING) & PLIB_USART_ErrorsGet(USART_ID_1) )
    {
        dummyData = PLIB_USART_ReceiverByteReceive(USART_ID_1);
        RXlength--;

        /* Try to flush error bytes for one full FIFO and exit instead of
         * blocking here if more error bytes are received*/
        if(0u == RXlength)
        {
            break;
        }
    }

    /* Ignore the warning */
    (void)dummyData;

    /* Clear error interrupt flag */
    SYS_INT_SourceStatusClear(INT_SOURCE_USART_1_ERROR);

    /* Clear up the receive interrupt flag so that RX interrupt is not
     * triggered for error bytes*/
    SYS_INT_SourceStatusClear(INT_SOURCE_USART_1_RECEIVE);
}



DRV_USART_BAUD_SET_RESULT DRV_USART0_BaudSet(uint32_t baud)
{
    uint32_t clockSource;
    int32_t brgValueLow=0;
    int32_t brgValueHigh=0;
    DRV_USART_BAUD_SET_RESULT retVal = DRV_USART_BAUD_SET_SUCCESS;
#if defined (PLIB_USART_ExistsModuleBusyStatus)
    bool isEnabled = false;
#endif

    /* Get the USART clock source value*/
    clockSource = SYS_CLK_PeripheralFrequencyGet ( CLK_BUS_PERIPHERAL_2 );

    /* Calculate low and high baud values */
    brgValueLow  = ( (clockSource/baud) >> 4 ) - 1;
    brgValueHigh = ( (clockSource/baud) >> 2 ) - 1;

#if defined (PLIB_USART_ExistsModuleBusyStatus)
        isEnabled = PLIB_USART_ModuleIsBusy (USART_ID_1);
        if (isEnabled)
        {
            PLIB_USART_Disable (USART_ID_1);
            while (PLIB_USART_ModuleIsBusy (USART_ID_1));
        }
#endif

    /* Check if the baud value can be set with high baud settings */
    if ((brgValueHigh >= 0) && (brgValueHigh <= UINT16_MAX))
    {
        PLIB_USART_BaudRateHighEnable(USART_ID_1);
        PLIB_USART_BaudRateHighSet(USART_ID_1,clockSource,baud);
    }

    /* Check if the baud value can be set with low baud settings */
    else if ((brgValueLow >= 0) && (brgValueLow <= UINT16_MAX))
    {
        PLIB_USART_BaudRateHighDisable(USART_ID_1);
        PLIB_USART_BaudRateSet(USART_ID_1, clockSource, baud);
    }
    else
    {
            retVal = DRV_USART_BAUD_SET_ERROR;
    }

#if defined (PLIB_USART_ExistsModuleBusyStatus)
    if (isEnabled)
    {
        PLIB_USART_Enable (USART_ID_1);
    }
#endif

    return retVal;
}


DRV_USART_LINE_CONTROL_SET_RESULT DRV_USART0_LineControlSet(DRV_USART_LINE_CONTROL lineControlMode)
{
#if defined (PLIB_USART_ExistsModuleBusyStatus)
    bool isEnabled = false;
#endif
#if defined (PLIB_USART_ExistsModuleBusyStatus)
        isEnabled = PLIB_USART_ModuleIsBusy (USART_ID_1);
        if (isEnabled)
        {
            PLIB_USART_Disable (USART_ID_1);
            while (PLIB_USART_ModuleIsBusy (USART_ID_1));
        }
#endif

    /* Set the Line Control Mode */
    PLIB_USART_LineControlModeSelect(USART_ID_1, lineControlMode);

#if defined (PLIB_USART_ExistsModuleBusyStatus)
        if (isEnabled)
        {
            PLIB_USART_Enable (USART_ID_1);
        }
#endif

    /* Return success */
    return(DRV_USART_LINE_CONTROL_SET_SUCCESS);
}

/*******************************************************************************
 End of File
*/

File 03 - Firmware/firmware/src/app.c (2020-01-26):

#include "app.h"

APP_DATA appData;

bool sigGenEnabled; //Enables signal generation
const float fSampling=49800.; //Sampling Frequency (49800 when PR2 = 1000)

unsigned long PA_COUNTER[18]; //Counter variable for timing
unsigned long PB_COUNTER[18];
unsigned long PC_COUNTER[18];
unsigned long PD_COUNTER[18];
unsigned long PE_COUNTER[18];
unsigned long PF_COUNTER[18];

unsigned long PA_COUNTER_DEFAULT[18]; //Default counter value gives phase angle for reset
unsigned long PB_COUNTER_DEFAULT[18];
unsigned long PC_COUNTER_DEFAULT[18];
unsigned long PD_COUNTER_DEFAULT[18];
unsigned long PE_COUNTER_DEFAULT[18];
unsigned long PF_COUNTER_DEFAULT[18];

unsigned long PA_ON[18]; //Counter position where it toggles port on
unsigned long PB_ON[18];
unsigned long PC_ON[18];
unsigned long PD_ON[18];
unsigned long PE_ON[18];
unsigned long PF_ON[18];

unsigned long PA_OFF[18]; //Counter position where it toggles port off
unsigned long PB_OFF[18];
unsigned long PC_OFF[18];
unsigned long PD_OFF[18];
unsigned long PE_OFF[18];
unsigned long PF_OFF[18];

unsigned int PORT_SHADOWREGISTERS[10]; //Register contains the values to be loaded into the ports at once after update

//Constants indicating which uC port corresponds to the physical output ports
const int PA_PORT[18]={9,9,9,1,1,1,7,7,7,7,0,0,1,8,8,8,8,1};
const int PB_PORT[18]={1,1,4,0,6,9,6,6,6,2,2,2,8,8,8,8,2,4};
const int PC_PORT[18]={4,4,0,6,4,4,4,6,6,6,4,4,8,8,8,8,0,0};
const int PD_PORT[18]={6,6,9,5,5,3,3,3,3,8,8,8,8,3,3,3,3,3};
const int PE_PORT[18]={2,2,3,7,7,7,7,3,3,3,0,0,9,9,9,5,5,0};
const int PF_PORT[18]={0,0,7,7,7,7,5,5,5,3,3,7,7,7,7,1,1,1};

//Constants indicating which uC port pin corresponds to the physical output port pins
const int PA_PIN[18]={3,2,1,11,10,8,3,2,1,0,10,9,2,15,14,13,11,4};
const int PB_PIN[18]={5,9,8,0,9,0,8,7,6,4,3,2,10,12,9,8,1,7};
const int PC_PIN[18]={6,5,5,15,4,3,2,13,12,14,1,0,7,6,5,4,7,6};
const int PD_PIN[18]={0,1,7,1,0,7,6,5,4,3,2,1,0,13,12,3,2,1};
const int PE_PIN[18]={14,13,0,15,14,13,12,11,10,9,15,14,6,5,4,5,4,4};
const int PF_PIN[18]={3,2,11,10,9,8,8,2,3,15,14,7,6,5,4,15,14,13};

//const unsigned int BITMASK_PORTB=0b0000001011001000; //NOT NEEDED

//Serial USB strings
char* outputString;
char* inputString;
char strCommand[4];
char PortStr[1];
char ChanStr[2];
char FreqStr[3];
char DutyStr[3];
char PhaseStr[3];

unsigned int txByte;
unsigned int rxByte;
const unsigned int rxBufferLimit=50;


void ResetCounters(){    
        //Resets all signal generator units to default OFF state                    
        int i;
        for (i=0;i<18;i++){
            //Reset counters to default phase angles
            PA_COUNTER[i]=PA_COUNTER_DEFAULT[i];
            PB_COUNTER[i]=PB_COUNTER_DEFAULT[i];
            PC_COUNTER[i]=PC_COUNTER_DEFAULT[i];
            PD_COUNTER[i]=PD_COUNTER_DEFAULT[i];
            PE_COUNTER[i]=PE_COUNTER_DEFAULT[i];
            PF_COUNTER[i]=PF_COUNTER_DEFAULT[i];
        }  
        
        for (i=0;i<10;i++){
            PORT_SHADOWREGISTERS[i]=0;
        }
            
        LATA=PORT_SHADOWREGISTERS[0];
        LATB=PORT_SHADOWREGISTERS[1];
        LATC=PORT_SHADOWREGISTERS[2];
        LATD=PORT_SHADOWREGISTERS[3];
        LATE=PORT_SHADOWREGISTERS[4];
        LATF=PORT_SHADOWREGISTERS[5];
        LATG=PORT_SHADOWREGISTERS[6];
        LATH=PORT_SHADOWREGISTERS[7];
        LATJ=PORT_SHADOWREGISTERS[8]; 
        LATK=PORT_SHADOWREGISTERS[9];   
            
}

void ZeroSigGen(){    
        //Resets all signal generator units to default OFF state                    
        int i;
        for (i=0;i<18;i++){
            //All counters will have zero duty cycle
            PA_ON[i]=PA_OFF[i];
            PB_ON[i]=PB_OFF[i];
            PC_ON[i]=PC_OFF[i];
            PD_ON[i]=PD_OFF[i];
            PE_ON[i]=PE_OFF[i];
            PF_ON[i]=PF_OFF[i];
        }  
        
        for (i=0;i<10;i++){
            PORT_SHADOWREGISTERS[i]=0;
        }
            
        LATA=PORT_SHADOWREGISTERS[0];
        LATB=PORT_SHADOWREGISTERS[1];
        LATC=PORT_SHADOWREGISTERS[2];
        LATD=PORT_SHADOWREGISTERS[3];
        LATE=PORT_SHADOWREGISTERS[4];
        LATF=PORT_SHADOWREGISTERS[5];
        LATG=PORT_SHADOWREGISTERS[6];
        LATH=PORT_SHADOWREGISTERS[7];
        LATJ=PORT_SHADOWREGISTERS[8]; 
        LATK=PORT_SHADOWREGISTERS[9];   
            
}

void APP_Initialize ( void )
{
    /* Place the App state machine in its initial state. */
    appData.state = APP_STATE_INIT;
    
}
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
